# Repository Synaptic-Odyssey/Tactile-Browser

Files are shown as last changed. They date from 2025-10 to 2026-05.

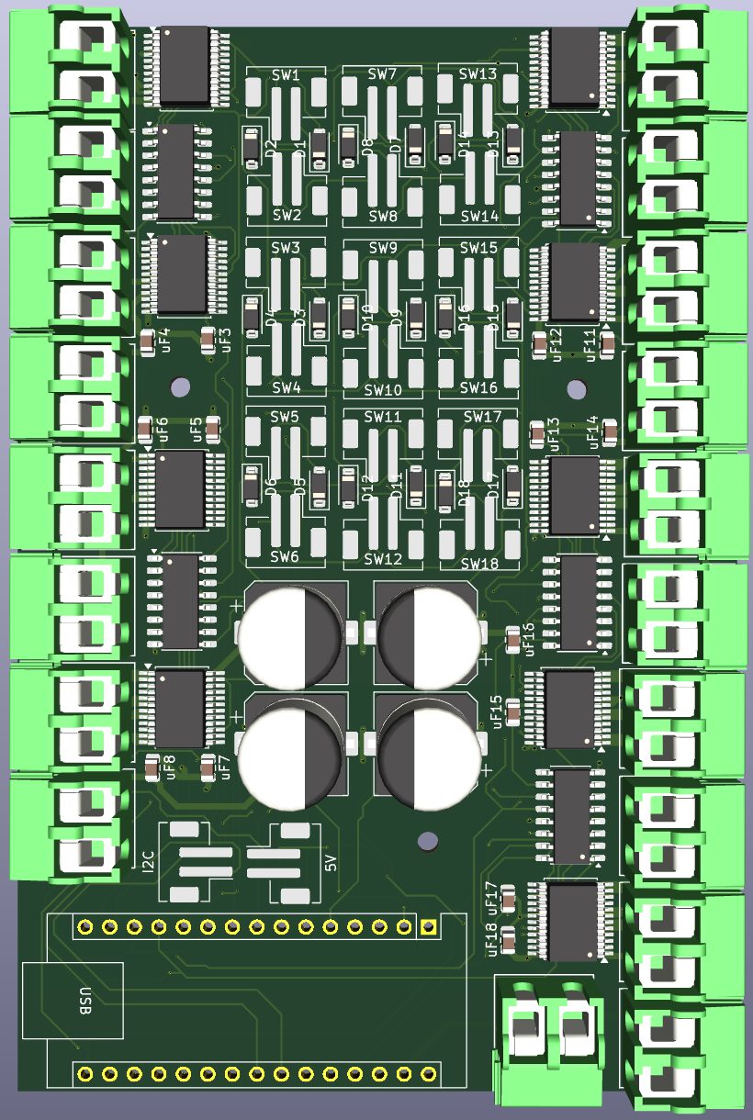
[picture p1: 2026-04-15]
IEEE_MWSCAS/IEEE_MWSCAS_Fig6.png

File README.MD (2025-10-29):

ABSTRACT:

This project aims to develop a tactile web browsing interface for blind and visually impaired users. Current assistive technology, such as screen readers, forces linear navigation through web pages, preventing users from perceiving spatial layout and efficiently locating interactive elements. The proposed system consists of a 17×11 grid of uniform keycaps (with keyswitches that double as input) that move along the Z-axis using bistable solenoids. Each grouping of blocks represents a distinct webpage element (e.g., headers, links, buttons). When a block is pressed down, the system provides audio feedback, reading the element’s content; prolonged touch can select the element and allow the user to interact with it. By mapping webpage structures into a physical tactile representation, users can explore content spatially and intuitively. Estimated cost for the prototype is ~$800. The project timeline spans two quarters, starting implementing webpage-to-grid mapping, then with the creation of a single 2x5 module, before integrating the entire design.

Detailed Presentation: https://docs.google.com/presentation/d/1p2b0jzcivFLc2I2OcCCj18AWDXcFEL55aIJLbLz9RJQ/edit?slide=id.g39ac1d9ecba_0_35#slide=id.g39ac1d9ecba_0_35

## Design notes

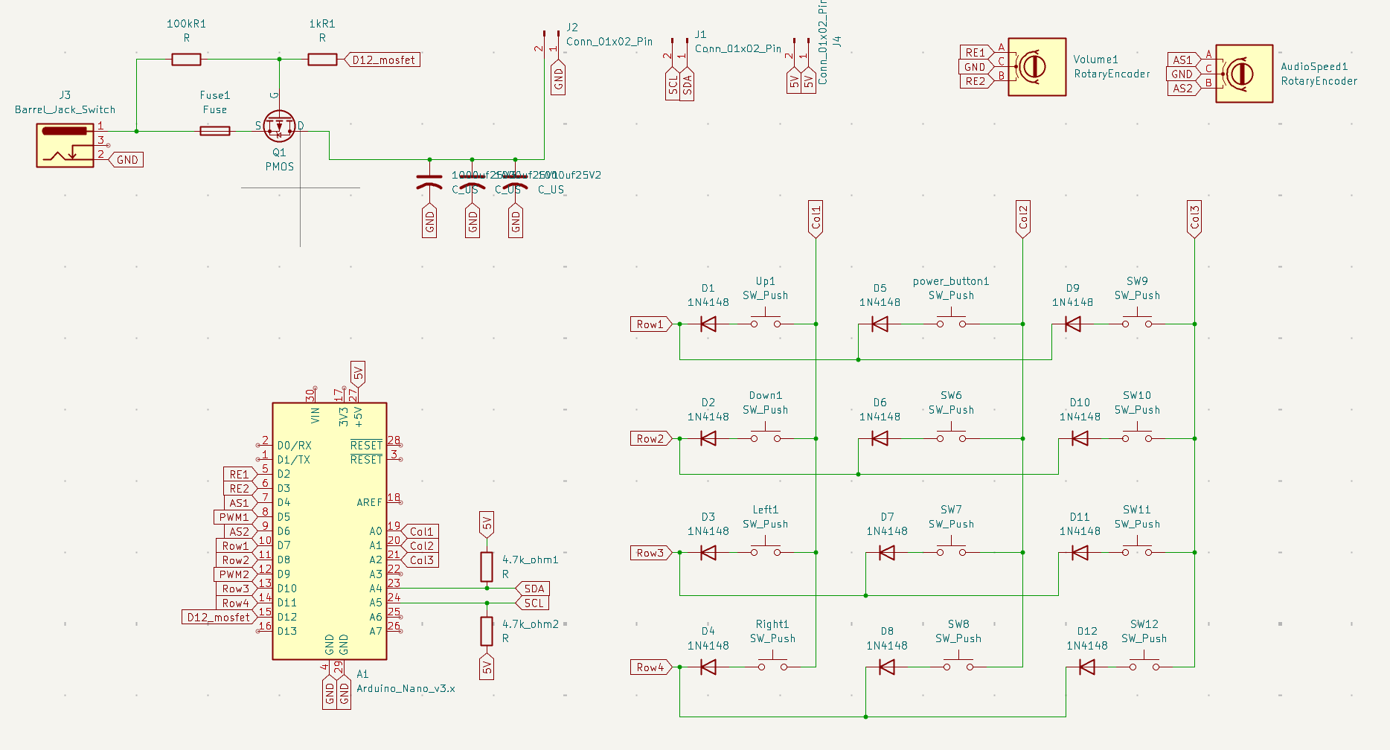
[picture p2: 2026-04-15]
IEEE_MWSCAS/IEEE_MWSCAS_Fig7.png

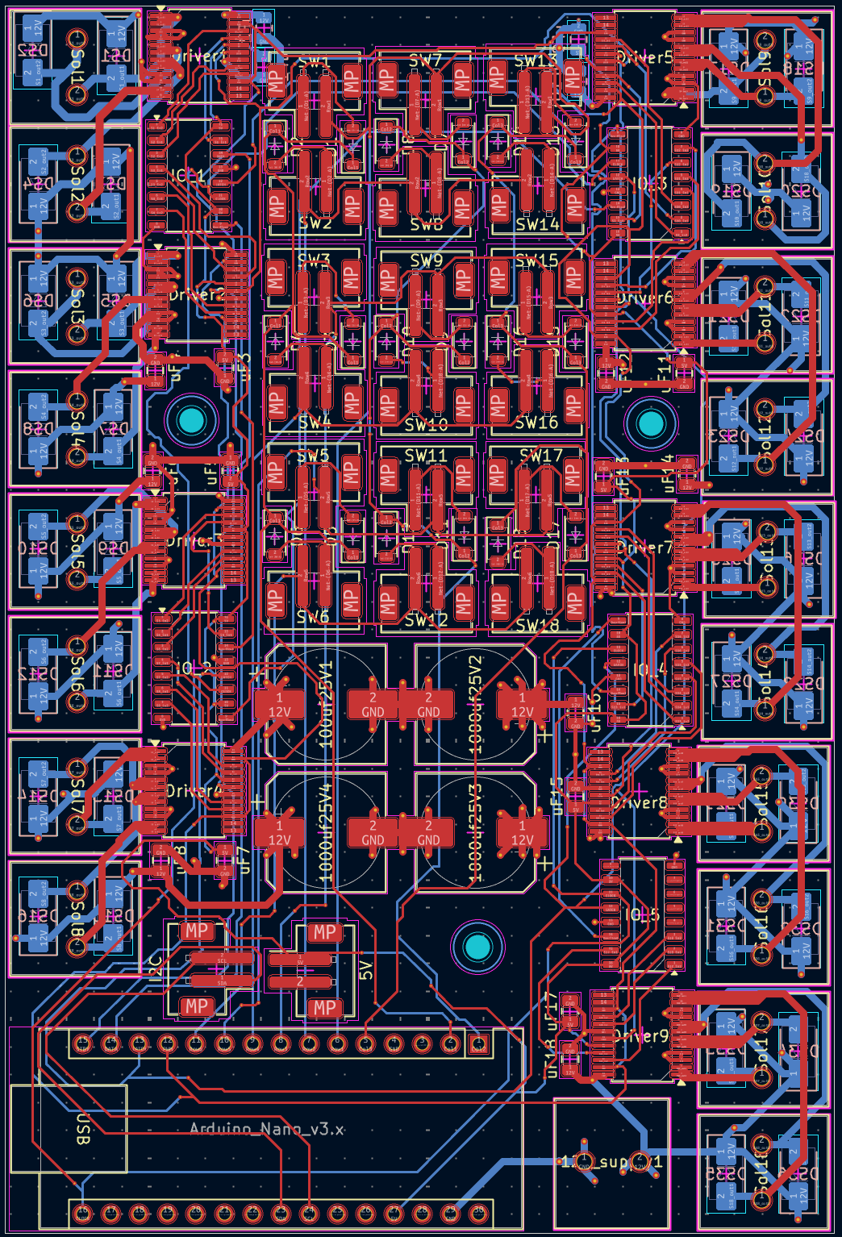
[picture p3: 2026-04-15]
IEEE_MWSCAS/IEEE_MWSCAS_Fig5.png

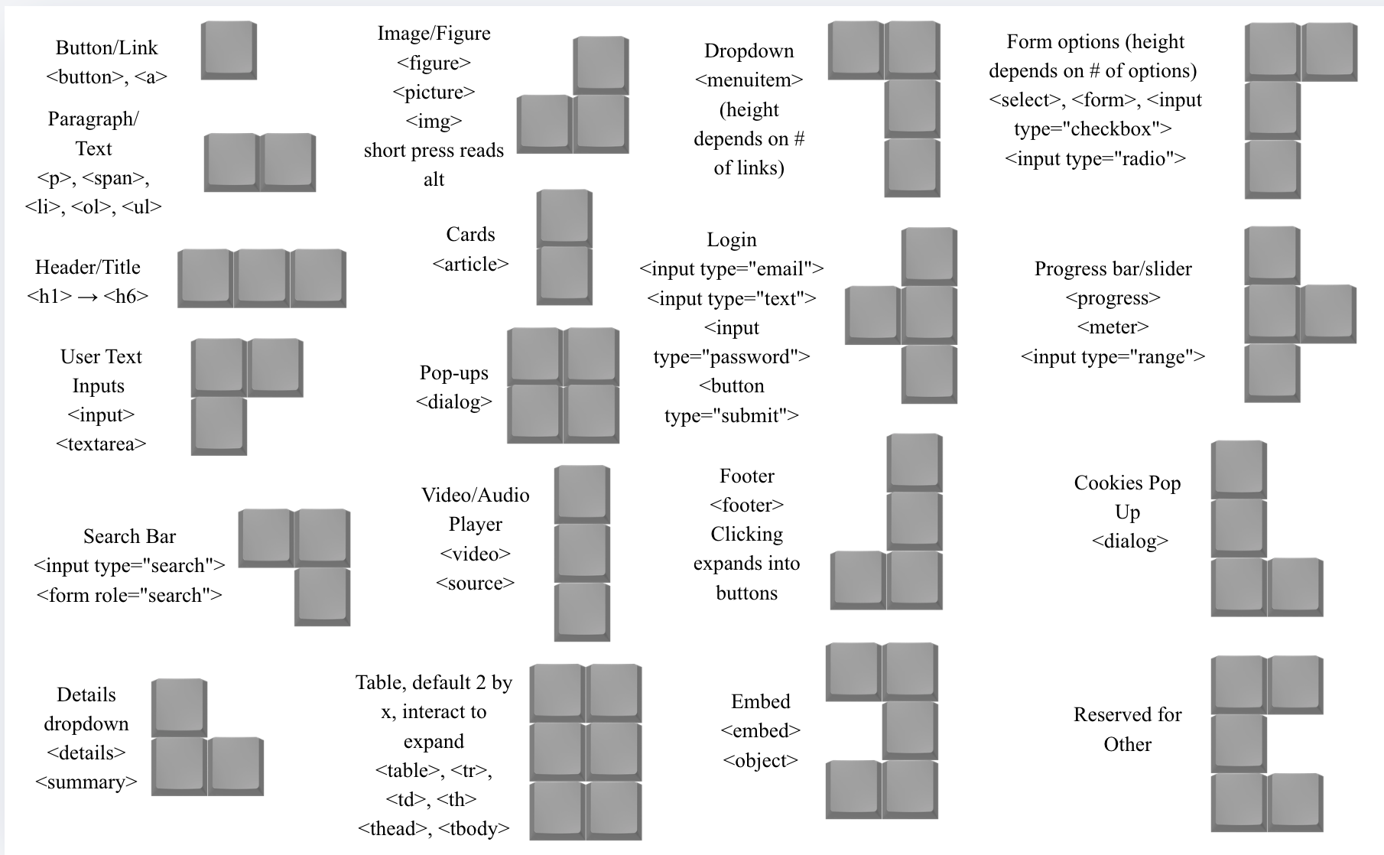
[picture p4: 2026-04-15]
IEEE_MWSCAS/IEEE_MWSCAS_Fig1.png

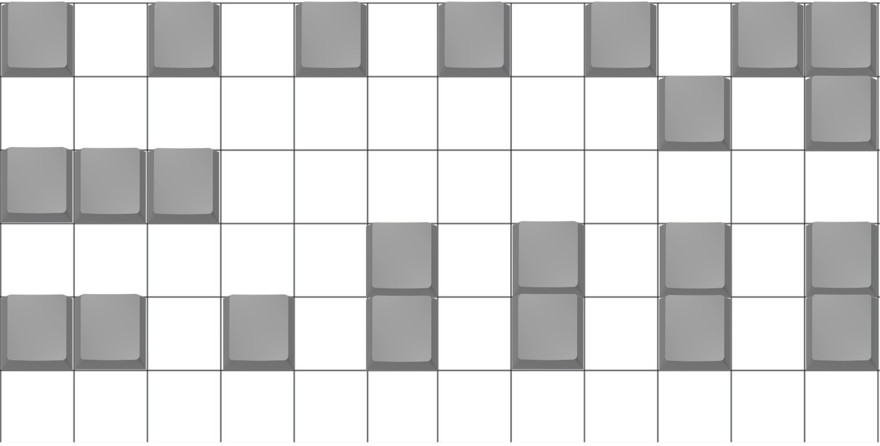
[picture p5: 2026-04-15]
IEEE_MWSCAS/IEEE_MWSCAS_Fig3.png

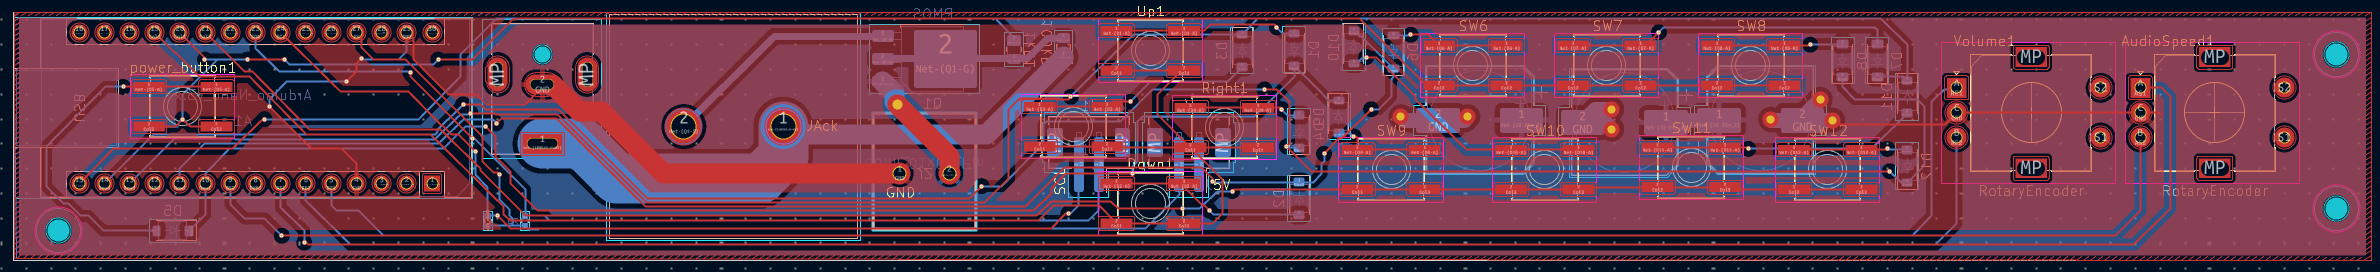
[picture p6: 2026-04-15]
IEEE_MWSCAS/IEEE_MWSCAS_Fig8.png

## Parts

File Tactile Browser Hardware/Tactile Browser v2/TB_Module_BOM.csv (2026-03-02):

Designator | Value | Footprint | Quantity | LCSC Part #
SW3,SW4,SW6,SW17,SW8,SW5,SW9,SW12,SW14,SW10,SW15,SW18,SW16,SW2,SW7,SW1,SW13,SW11 | SW_Push | JST_PH_B2B-PH-SM4-TB_1x02-1MP_P2.00mm_Vertical | 18 | C160352
uF7,uF18,uF8,uF5,uF11,uF16,uF4,uF3,uF12,uF6,uF15,uF14,uF17,uF13,uF2,uF1,uF9,uF10 | C | C_0805_2012Metric | 18 | C141772
Driver8,Driver5,Driver6,Driver7,Driver2,Driver4,Driver1,Driver9,Driver3 | TB6612FNG | SSOP-24_5.3x8.2mm_P0.65mm | 9 | C141517
D1,D14,D13,D3,D7,D18,D9,D10,D17,D2,D16,D8,D15,D5,D11,D6,D12,D4 | 1N4148 | D_SOD-123 | 18 | C917030
1000uf25V2,1000uf25V4,100uf25V1,1000uf25V3 | C_Polarized | CP_Elec_10x12.5 | 4 | C49256851
Sol5,12V_supply1,Sol18,Sol9,Sol17,Sol15,Sol13,Sol14,Sol8,Sol2,Sol7,Sol1,Sol12,Sol3,Sol11,Sol6,Sol16,Sol4,Sol10 | Conn_01x02_Pin | ScrewTerminal_Vertical_1935310 | 19 | C6395113
IO_1,IO_5,IO_4,IO_2,IO_3 | 74HC595 | JEITA_SOIC-16_3.9x9.9mm_P1.27mm | 5 | C5947
5V | Conn_01x01_Pin | JST_PH_B2B-PH-SM4-TB_1x02-1MP_P2.00mm_Vertical | 1 | C160352
I2C | Conn_01x02_Pin | JST_PH_B2B-PH-SM4-TB_1x02-1MP_P2.00mm_Vertical | 1 | C160352
A1 | Arduino_Nano_v3.x | Arduino_Nano | 1 | HAND_SOLDER
DS22,DS10,DS8,DS27,DS9,DS36,DS26,DS12,DS5,DS15,DS19,DS30,DS7,DS1,DS35,DS24,DS3,DS17,DS6,DS34,DS13,DS28,DS25,DS14,DS31,DS2,DS4,DS18,DS16,DS32,DS29,DS21,DS20,DS33,DS23,DS11 | D_Schottky | D_SMA | 36 | C83852

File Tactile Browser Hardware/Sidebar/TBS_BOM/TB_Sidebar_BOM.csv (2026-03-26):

Designator | Comment | Footprint | LCSC Part #
Volume1 | RotaryEncoder | RotaryEncoder_Alps_EC11E-Switch_Vertical_H20mm | HAND_SOLDER
AudioSpeed1 | RotaryEncoder | RotaryEncoder_Alps_EC11E-Switch_Vertical_H20mm | HAND_SOLDER
power_button1 | SW_Push | SW_SPST_EVQQ2 | C2976606
Right1 | SW_Push | SW_SPST_EVQQ2 | C2976606
Down1 | SW_Push | SW_SPST_EVQQ2 | C2976606
SW10 | SW_Push | SW_SPST_EVQQ2 | C2976606
Left1 | SW_Push | SW_SPST_EVQQ2 | C2976606
SW8 | SW_Push | SW_SPST_EVQQ2 | C2976606
SW6 | SW_Push | SW_SPST_EVQQ2 | C2976606
Up1 | SW_Push | SW_SPST_EVQQ2 | C2976606
SW12 | SW_Push | SW_SPST_EVQQ2 | C2976606
SW11 | SW_Push | SW_SPST_EVQQ2 | C2976606
SW7 | SW_Push | SW_SPST_EVQQ2 | C2976606
SW9 | SW_Push | SW_SPST_EVQQ2 | C2976606
1kR1 | R | R_0805_2012Metric | C727989
100kR1 | R | R_0805_2012Metric | C161786
A1 | Arduino_Nano_v3.x | Arduino_Nano | HAND_SOLDER
1000uf25V2 | C_US | CP_Elec_10x12.5 | C49256851
1000uf25V3 | C_US | CP_Elec_10x12.5 | C49256851
1000uf25V1 | C_US | CP_Elec_10x12.5 | C49256851
D8 | 1N4148 | D_SOD-123 | C917030
D9 | 1N4148 | D_SOD-123 | C917030
D10 | 1N4148 | D_SOD-123 | C917030
D5 | 1N4148 | D_SOD-123 | C917030
D6 | 1N4148 | D_SOD-123 | C917030
D12 | 1N4148 | D_SOD-123 | C917030
D11 | 1N4148 | D_SOD-123 | C917030
D3 | 1N4148 | D_SOD-123 | C917030
D2 | 1N4148 | D_SOD-123 | C917030
D1 | 1N4148 | D_SOD-123 | C917030
D4 | 1N4148 | D_SOD-123 | C917030
D7 | 1N4148 | D_SOD-123 | C917030
Q1 | PMOS | TO-252-3_TabPin2 | HAND_SOLDER
Fuse1 | Fuse | FUSE_3560 | HAND_SOLDER
J2 | Conn_01x02_Pin | ScrewTerminal_Vertical_1935310 | HAND_SOLDER
J4 | Conn_01x02_Pin | JST_PH_B2B-PH-SM4-TB_1x02-1MP_P2.00mm_Vertical | C160352
J1 | Conn_01x02_Pin | JST_PH_B2B-PH-SM4-TB_1x02-1MP_P2.00mm_Vertical | C160352
4.7k_ohm2 | R | R_0402_1005Metric | C105871
4.7k_ohm1 | R | R_0402_1005Metric | C105871
J3 | Barrel_Jack_Switch | BarrelJack_CUI_PJ-063AH_Horizontal | HAND_SOLDER

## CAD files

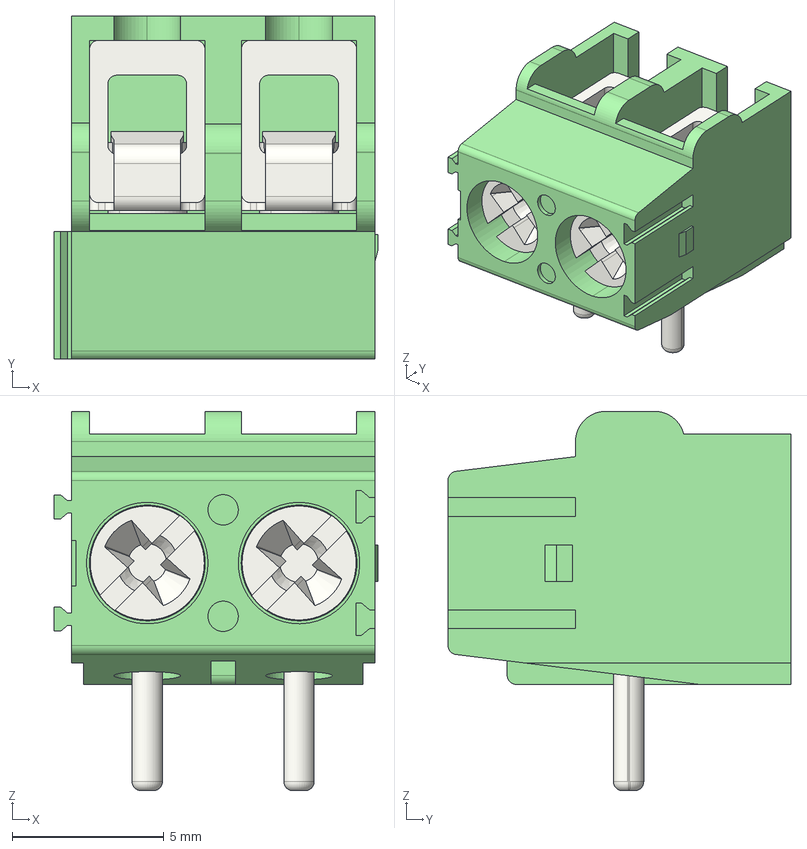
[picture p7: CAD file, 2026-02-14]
Tactile Browser Hardware/Tactile Browser v2/pxc_1935310_07_02_PT-1-5-2-5-0-V_3D.stp
10.7 x 11.3 x 12.5 mm

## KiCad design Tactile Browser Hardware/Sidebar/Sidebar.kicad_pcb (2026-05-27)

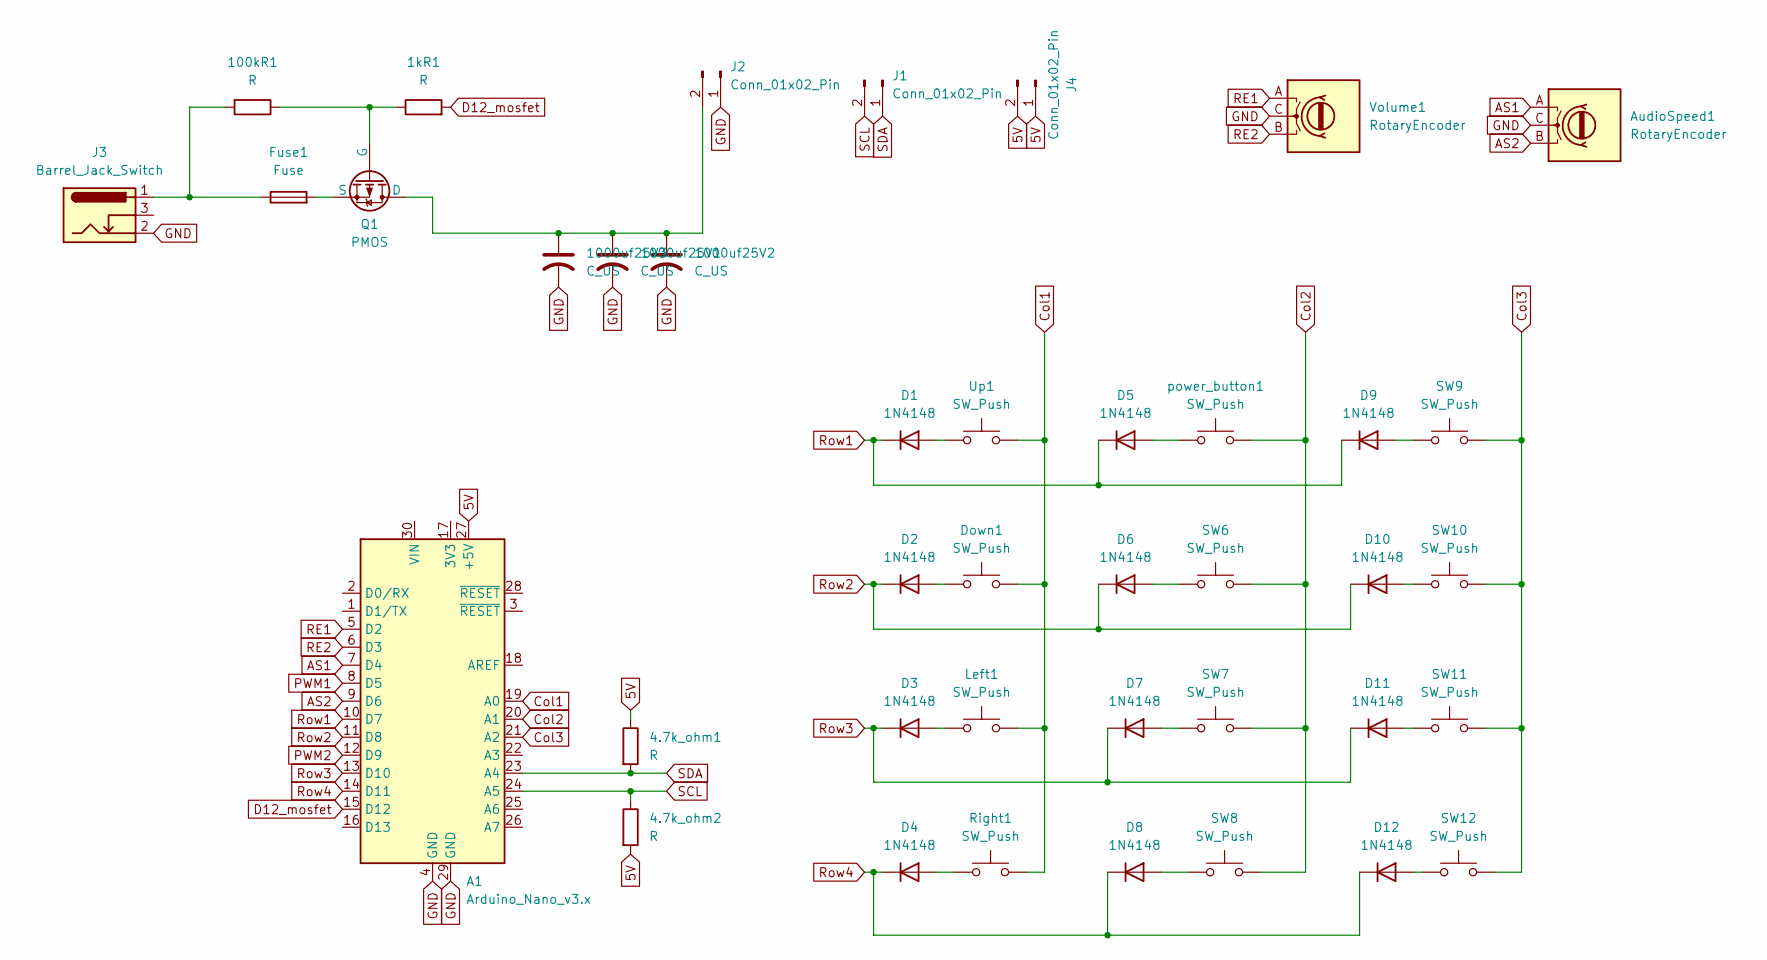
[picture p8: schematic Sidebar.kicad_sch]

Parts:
1kR1, 100kR1: R; R_0805_2012Metric
4.7k_ohm1, 4.7k_ohm2: R; R_0402_1005Metric
1000uf25V1, 1000uf25V2, 1000uf25V3: C_US; CP_Elec_10x12.5
A1: Arduino_Nano_v3.x; Arduino_Nano
AudioSpeed1: RotaryEncoder; RotaryEncoder_Alps_EC11E-Switch_Vertical_H20mm
D1, D2, D3, D4, D5, D6, D7, D8, D9, D10, D11, D12: 1N4148; D_SOD-123
Down1: SW_Push; SW_SPST_EVQQ2
Fuse1: Fuse; FUSE_3560
J1, J4: Conn_01x02_Pin; JST_PH_B2B-PH-SM4-TB_1x02-1MP_P2.00mm_Vertical
J2: Conn_01x02_Pin; ScrewTerminal_Vertical_1935310
J3: Barrel_Jack_Switch; BarrelJack_CUI_PJ-063AH_Horizontal
Left1: SW_Push; SW_SPST_EVQQ2
Q1: PMOS; TO-252-3_TabPin2
Right1: SW_Push; SW_SPST_EVQQ2
SW6, SW7, SW8, SW9, SW10, SW11, SW12: SW_Push; SW_SPST_EVQQ2
Up1: SW_Push; SW_SPST_EVQQ2
Volume1: RotaryEncoder; RotaryEncoder_Alps_EC11E-Switch_Vertical_H20mm
power_button1: SW_Push; SW_SPST_EVQQ2

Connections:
5V: 4.7k_ohm1.1, 4.7k_ohm2.2, A1.27 (+5V), J4.1, J4.2
AS1: A1.7 (D4), AudioSpeed1.A
AS2: A1.9 (D6), AudioSpeed1.B
Col1: A1.19 (A0), Down1.2, Left1.2, Right1.2, Up1.2
Col2: A1.20 (A1), SW6.2, SW7.2, SW8.2, power_button1.2
Col3: A1.21 (A2), SW9.2, SW10.2, SW11.2, SW12.2
D12_mosfet: 1kR1.2, A1.15 (D12); also elsewhere on the board
GND: 1000uf25V1.2, 1000uf25V2.2, 1000uf25V3.2, A1.4 (GND), A1.29 (GND), AudioSpeed1.C, J2.1, J3.2, Volume1.C
unnamed 8: 100kR1.2, Fuse1.1, J3.1; also elsewhere on the board
unnamed: D1.2 (A), Up1.1
unnamed: D2.2 (A), Down1.1
unnamed: D3.2 (A), Left1.1
unnamed: D4.2 (A), Right1.1
unnamed: D5.2 (A), power_button1.1
unnamed: D6.2 (A), SW6.1
unnamed: D7.2 (A), SW7.1
unnamed: D8.2 (A), SW8.1
unnamed: D9.2 (A), SW9.1
unnamed: D10.2 (A), SW10.1
unnamed: D11.2 (A), SW11.1
unnamed: D12.2 (A), SW12.1
unnamed: 1000uf25V1.1, 1000uf25V2.1, 1000uf25V3.1, J2.2, Q1.1 (D)
unnamed 22: 1kR1.1, 100kR1.1, Q1.2 (G); also elsewhere on the board
unnamed: Fuse1.2, Q1.3 (S)
PWM1: A1.8 (D5)
PWM2: A1.12 (D9)
RE1: A1.5 (D2), Volume1.A
RE2: A1.6 (D3), Volume1.B
Row1: A1.10 (D7), D1.1 (K), D5.1 (K), D9.1 (K)
Row2: A1.11 (D8), D2.1 (K), D6.1 (K), D10.1 (K)
Row3: A1.13 (D10), D3.1 (K), D7.1 (K), D11.1 (K)
Row4: A1.14 (D11), D4.1 (K), D8.1 (K), D12.1 (K)
SCL: 4.7k_ohm2.1, A1.24 (A5), J1.2
SDA: 4.7k_ohm1.2, A1.23 (A4), J1.1

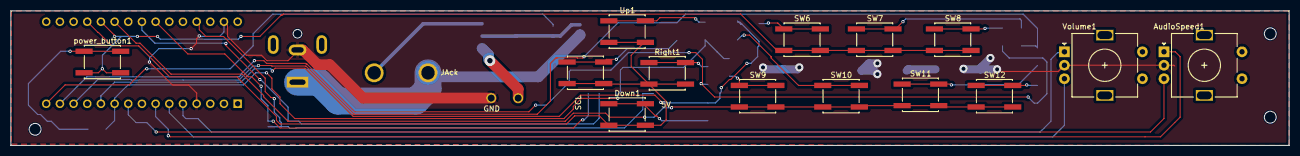
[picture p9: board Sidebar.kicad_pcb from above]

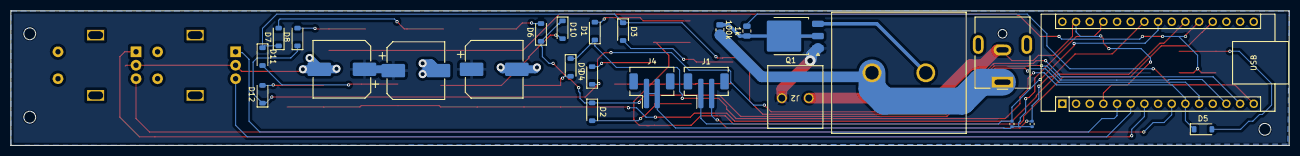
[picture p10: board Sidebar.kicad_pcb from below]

Board: 2 copper layers, 237.5 x 25.0 mm, 40 parts (26 on the bottom side), 32 nets.

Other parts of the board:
1k, 100k: R; R_0805_2012Metric

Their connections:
D12_mosfet: 1k.2; also elsewhere on the board
unnamed 8: 100k.2; also elsewhere on the board
unnamed 22: 1k.1, 100k.1; also elsewhere on the board

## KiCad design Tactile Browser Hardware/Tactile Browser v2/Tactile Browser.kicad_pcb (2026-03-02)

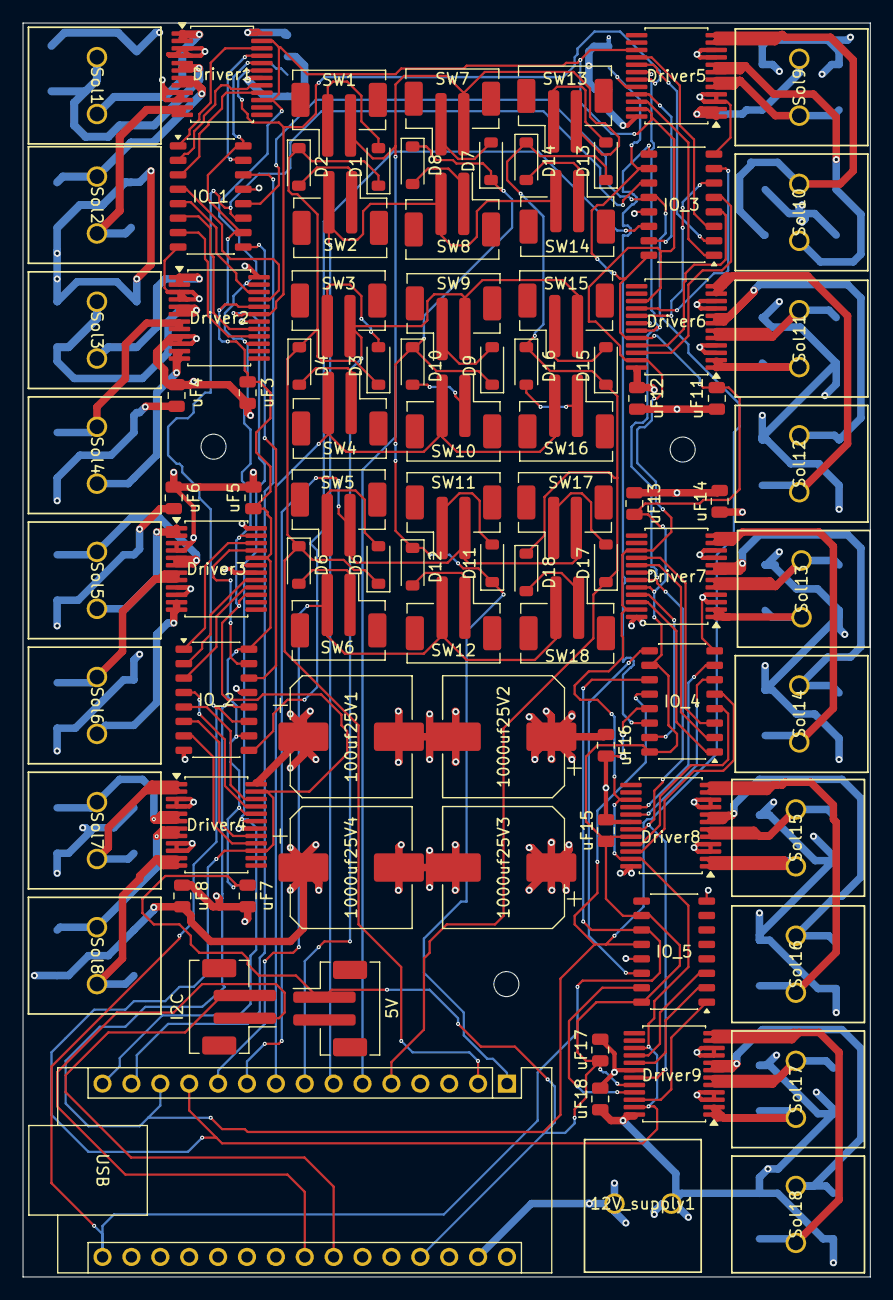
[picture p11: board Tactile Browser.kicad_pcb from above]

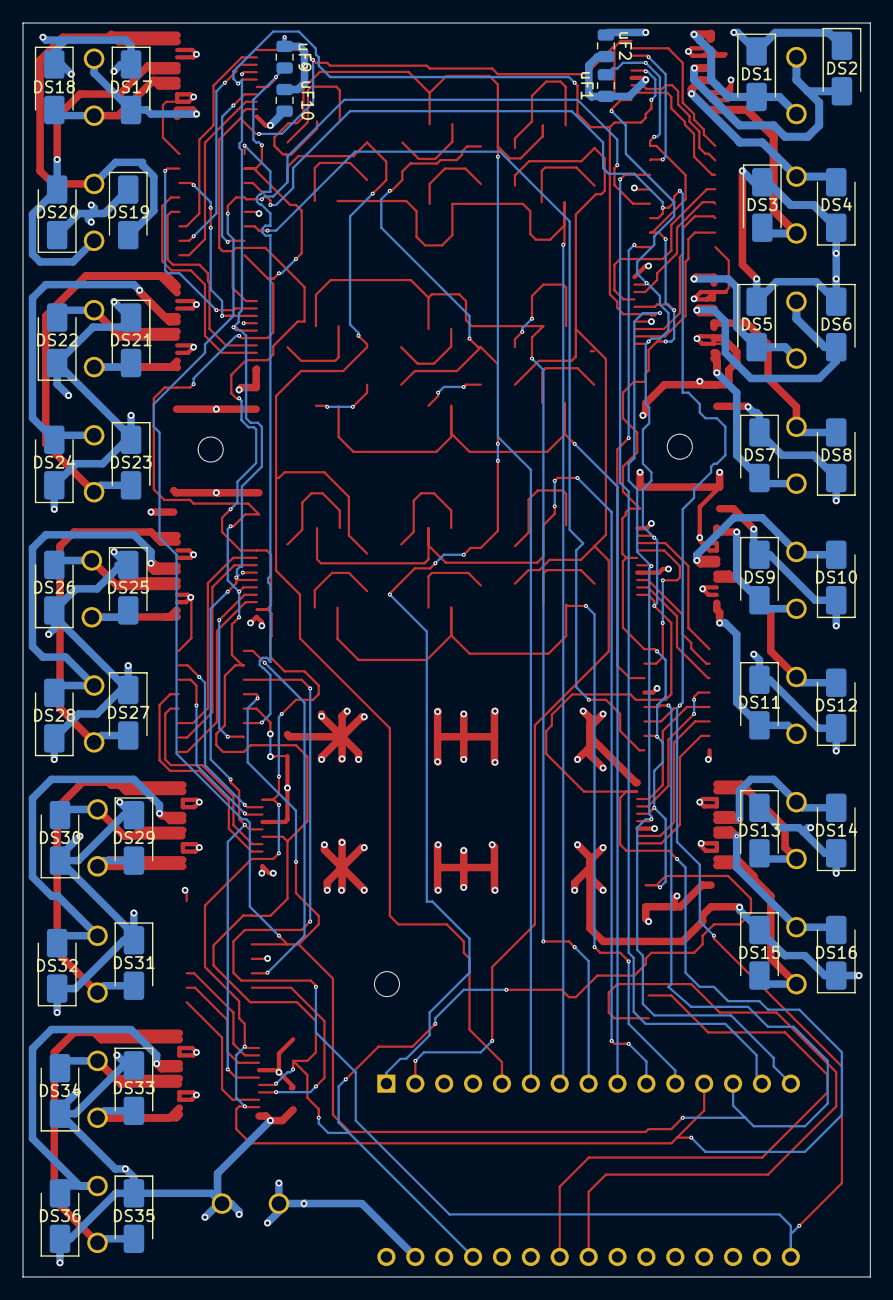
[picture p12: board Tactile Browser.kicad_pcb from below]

Board: 4 copper layers, 74.5 x 110.2 mm, 130 parts (40 on the bottom side), 113 nets.

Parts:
5V: Conn_01x01_Pin; JST_PH_B2B-PH-SM4-TB_1x02-1MP_P2.00mm_Vertical
12V_supply1: Conn_01x02_Pin; ScrewTerminal_Vertical_1935310
100uf25V1, 1000uf25V2, 1000uf25V3, 1000uf25V4: C_Polarized; CP_Elec_10x12.5
A1: Arduino_Nano_v3.x; Arduino_Nano
D1, D2, D3, D4, D5, D6, D7, D8, D9, D10, D11, D12, D13, D14, D15, D16, D17, D18: 1N4148; D_SOD-123
DS1, DS2, DS3, DS4, DS5, DS6, DS7, DS8, DS9, DS10, DS11, DS12, DS13, DS14, DS15, DS16, DS17, DS18, DS19, DS20, DS21, DS22, DS23, DS24, DS25, DS26, DS27, DS28, DS29, DS30, DS31, DS32, DS33, DS34, DS35, DS36: D_Schottky; D_SMA
Driver1, Driver2, Driver3, Driver4, Driver5, Driver6, Driver7, Driver8, Driver9: TB6612FNG; SSOP-24_5.3x8.2mm_P0.65mm
I2C: Conn_01x02_Pin; JST_PH_B2B-PH-SM4-TB_1x02-1MP_P2.00mm_Vertical
IO_1, IO_2, IO_3, IO_4, IO_5: 74HC595; JEITA_SOIC-16_3.9x9.9mm_P1.27mm
SW1, SW2, SW3, SW4, SW5, SW6, SW7, SW8, SW9, SW10, SW11, SW12, SW13, SW14, SW15, SW16, SW17, SW18: SW_Push; JST_PH_B2B-PH-SM4-TB_1x02-1MP_P2.00mm_Vertical
Sol1, Sol2, Sol3, Sol4, Sol5, Sol6, Sol7, Sol8, Sol9, Sol10, Sol11, Sol12, Sol13, Sol14, Sol15, Sol16, Sol17, Sol18: Conn_01x02_Pin; ScrewTerminal_Vertical_1935310
uF1, uF2, uF3, uF4, uF5, uF6, uF7, uF8, uF9, uF10, uF11, uF12, uF13, uF14, uF15, uF16, uF17, uF18: C; C_0805_2012Metric

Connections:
5V: 5V.1, A1.27 (+5V), Driver1.20 (VCC), Driver2.20 (VCC), Driver3.20 (VCC), Driver4.20 (VCC), Driver5.20 (VCC), Driver6.20 (VCC), Driver7.20 (VCC), Driver8.20 (VCC), Driver9.20 (VCC), IO_1.10 (~SRCLR), IO_1.16 (VCC), IO_2.10 (~SRCLR), IO_2.16 (VCC), IO_3.10 (~SRCLR), IO_3.16 (VCC), IO_4.10 (~SRCLR), IO_4.16 (VCC), IO_5.10 (~SRCLR), IO_5.16 (VCC), uF1.2, uF3.2, uF5.2, uF7.1, uF9.1, uF11.1, uF13.1, uF15.1, uF17.1
12V: 12V_supply1.2, 100uf25V1.1, 1000uf25V2.1, 1000uf25V3.1, 1000uf25V4.1, DS1.1 (K), DS2.1 (K), DS3.1 (K), DS4.1 (K), DS5.1 (K), DS6.1 (K), DS7.1 (K), DS8.1 (K), DS9.1 (K), DS10.1 (K), DS11.1 (K), DS12.1 (K), DS13.1 (K), DS14.1 (K), DS15.1 (K), DS16.1 (K), DS17.1 (K), DS18.1 (K), DS19.1 (K), DS20.1 (K), DS21.1 (K), DS22.1 (K), DS23.1 (K), DS24.1 (K), DS25.1 (K), DS26.1 (K), DS27.1 (K), DS28.1 (K), DS29.1 (K), DS30.1 (K), DS31.1 (K), DS32.1 (K), DS33.1 (K), DS34.1 (K), DS35.1 (K), DS36.1 (K), Driver1.24 (VM1), Driver2.24 (VM3), Driver3.24 (VM1), Driver4.24 (VM1), Driver5.24 (VM3), Driver6.24 (VM1), Driver7.24 (VM3), Driver8.24 (VM3), Driver9.24 (VM3), uF2.1, uF4.1, uF6.1, uF8.1, uF10.1, uF12.1, uF14.1, uF16.1, uF18.1
CLOCK: A1.16 (D13), IO_1.11 (SRCLK), IO_2.11 (SRCLK), IO_3.11 (SRCLK), IO_4.11 (SRCLK), IO_5.11 (SRCLK)
Col1: A1.2 (D0/RX), D1.1 (K), D2.1 (K), D3.1 (K), D4.1 (K), D5.1 (K), D6.1 (K)
Col2: A1.1 (D1/TX), D7.1 (K), D8.1 (K), D9.1 (K), D10.1 (K), D11.1 (K), D12.1 (K)
Col3: A1.5 (D2), D13.1 (K), D14.1 (K), D15.1 (K), D16.1 (K), D17.1 (K), D18.1 (K)
DATA: A1.14 (D11), IO_1.14 (SER)
GND: 12V_supply1.1, 100uf25V1.2, 1000uf25V2.2, 1000uf25V3.2, 1000uf25V4.2, A1.4 (GND), A1.29 (GND), Driver1.3 (PGND1), Driver1.4 (PGND1), Driver1.9 (PGND2), Driver1.10 (PGND2), Driver1.18 (GND), Driver2.3 (PGND1), Driver2.4 (PGND1), Driver2.9 (PGND2), Driver2.10 (PGND2), Driver2.18 (GND), Driver3.3 (PGND1), Driver3.4 (PGND1), Driver3.9 (PGND2), Driver3.10 (PGND2), Driver3.18 (GND), Driver4.3 (PGND1), Driver4.4 (PGND1), Driver4.9 (PGND2), Driver4.10 (PGND2), Driver4.18 (GND), Driver5.3 (PGND1), Driver5.4 (PGND1), Driver5.9 (PGND2), Driver5.10 (PGND2), Driver5.18 (GND), Driver6.3 (PGND1), Driver6.4 (PGND1), Driver6.9 (PGND2), Driver6.10 (PGND2), Driver6.18 (GND), Driver7.3 (PGND1), Driver7.4 (PGND1), Driver7.9 (PGND2), Driver7.10 (PGND2), Driver7.18 (GND), Driver8.3 (PGND1), Driver8.4 (PGND1), Driver8.9 (PGND2), Driver8.10 (PGND2), Driver8.18 (GND), Driver9.3 (PGND1), Driver9.4 (PGND1), Driver9.9 (PGND2), Driver9.10 (PGND2), Driver9.18 (GND), IO_1.8 (GND), IO_1.13 (~OE), IO_2.8 (GND), IO_2.13 (~OE), IO_3.8 (GND), IO_3.13 (~OE), IO_4.8 (GND), IO_4.13 (~OE), IO_5.8 (GND), IO_5.13 (~OE), uF1.1, uF2.2, uF3.1, uF4.2, uF5.1, uF6.2, uF7.2, uF8.2, uF9.2, uF10.2, uF11.2, uF12.2, uF13.2, uF14.2, uF15.2, uF16.2, uF17.2, uF18.2
LATCH: A1.13 (D10), IO_1.12 (RCLK), IO_2.12 (RCLK), IO_3.12 (RCLK), IO_4.12 (RCLK), IO_5.12 (RCLK)
unnamed: D1.2 (A), SW1.1
unnamed: D2.2 (A), SW2.1
unnamed: D3.2 (A), SW3.1
unnamed: D4.2 (A), SW4.1
unnamed: D5.2 (A), SW5.1
unnamed: D6.2 (A), SW6.1
unnamed: D7.2 (A), SW7.1
unnamed: D8.2 (A), SW8.1
unnamed: D9.2 (A), SW9.1
unnamed: D10.2 (A), SW10.1
unnamed: D11.2 (A), SW11.1
unnamed: D12.2 (A), SW12.1
unnamed: D13.2 (A), SW13.1
unnamed: D14.2 (A), SW14.1
unnamed: D15.2 (A), SW15.1
unnamed: D16.2 (A), SW16.1
unnamed: D17.2 (A), SW17.1
unnamed: D18.2 (A), SW18.1
Overflow1: IO_1.9 (QH'), IO_2.14 (SER)
Overflow2: IO_2.9 (QH'), IO_3.14 (SER)
Overflow3: IO_3.9 (QH'), IO_4.14 (SER)
Overflow4: IO_4.9 (QH'), IO_5.14 (SER)
PWM: A1.12 (D9), Driver1.15 (PWMB), Driver1.23 (PWMA), Driver2.15 (PWMB), Driver2.23 (PWMA), Driver3.15 (PWMB), Driver3.23 (PWMA), Driver4.15 (PWMB), Driver4.23 (PWMA), Driver5.15 (PWMB), Driver5.23 (PWMA), Driver6.15 (PWMB), Driver6.23 (PWMA), Driver7.15 (PWMB), Driver7.23 (PWMA), Driver8.15 (PWMB), Driver8.23 (PWMA), Driver9.15 (PWMB), Driver9.23 (PWMA)
Row1: A1.6 (D3), SW1.2, SW7.2, SW13.2
Row2: A1.7 (D4), SW2.2, SW8.2, SW14.2
Row3: A1.8 (D5), SW3.2, SW9.2, SW15.2
Row4: A1.9 (D6), SW4.2, SW10.2, SW16.2
Row5: A1.10 (D7), SW5.2, SW11.2, SW17.2
Row6: A1.11 (D8), SW6.2, SW12.2, SW18.2
S1_in1: Driver1.21 (AIN1), IO_1.15 (QA)
S1_in2: Driver1.22 (AIN2), IO_1.1 (QB)
S1_out1: DS1.2 (A), Driver1.1 (AO1), Driver1.2 (AO1), Sol1.2
S1_out2: DS2.2 (A), Driver1.5 (AO2), Driver1.6 (AO2), Sol1.1
S2_in1: Driver1.17 (BIN1), IO_1.2 (QC)
S2_in2: Driver1.16 (BIN2), IO_1.3 (QD)
S2_out1: DS3.2 (A), Driver1.11 (BO1), Driver1.12 (BO1), Sol2.2
S2_out2: DS4.2 (A), Driver1.7 (BO2), Driver1.8 (BO2), Sol2.1
S3_in1: Driver2.21 (AIN1), IO_1.4 (QE)
S3_in2: Driver2.22 (AIN2), IO_1.5 (QF)
S3_out1: DS5.2 (A), Driver2.1 (AO1), Driver2.2 (AO1), Sol3.2
S3_out2: DS6.2 (A), Driver2.5 (AO2), Driver2.6 (AO2), Sol3.1
S4_in1: Driver2.17 (BIN1), IO_1.6 (QG)
S4_in2: Driver2.16 (BIN2), IO_1.7 (QH)
S4_out1: DS7.2 (A), Driver2.11 (BO1), Driver2.12 (BO1), Sol4.2
S4_out2: DS8.2 (A), Driver2.7 (BO2), Driver2.8 (BO2), Sol4.1
S5_in1: Driver3.21 (AIN1), IO_2.15 (QA)
S5_in2: Driver3.22 (AIN2), IO_2.1 (QB)
S5_out1: DS9.2 (A), Driver3.1 (AO1), Driver3.2 (AO1), Sol5.2
S5_out2: DS10.2 (A), Driver3.5 (AO2), Driver3.6 (AO2), Sol5.1
S6_in1: Driver3.17 (BIN1), IO_2.2 (QC)
S6_in2: Driver3.16 (BIN2), IO_2.3 (QD)
S6_out1: DS11.2 (A), Driver3.11 (BO1), Driver3.12 (BO1), Sol6.2
S6_out2: DS12.2 (A), Driver3.7 (BO2), Driver3.8 (BO2), Sol6.1
S7_in1: Driver4.21 (AIN1), IO_2.4 (QE)
S7_in2: Driver4.22 (AIN2), IO_2.5 (QF)
S7_out1: DS13.2 (A), Driver4.1 (AO1), Driver4.2 (AO1), Sol7.2
S7_out2: DS14.2 (A), Driver4.5 (AO2), Driver4.6 (AO2), Sol7.1
S8_in1: Driver4.17 (BIN1), IO_2.6 (QG)
S8_in2: Driver4.16 (BIN2), IO_2.7 (QH)
S8_out1: DS15.2 (A), Driver4.11 (BO1), Driver4.12 (BO1), Sol8.2
S8_out2: DS16.2 (A), Driver4.7 (BO2), Driver4.8 (BO2), Sol8.1
S9_in1: Driver5.21 (AIN1), IO_3.15 (QA)
S9_in2: Driver5.22 (AIN2), IO_3.1 (QB)
S9_out1: DS17.2 (A), Driver5.1 (AO1), Driver5.2 (AO1), Sol9.2
S9_out2: DS18.2 (A), Driver5.5 (AO2), Driver5.6 (AO2), Sol9.1
S10_in1: Driver5.17 (BIN1), IO_3.2 (QC)
S10_in2: Driver5.16 (BIN2), IO_3.3 (QD)
S10_out1: DS19.2 (A), Driver5.11 (BO1), Driver5.12 (BO1), Sol10.2
S10_out2: DS20.2 (A), Driver5.7 (BO2), Driver5.8 (BO2), Sol10.1
S11_in1: Driver6.21 (AIN1), IO_3.4 (QE)
S11_in2: Driver6.22 (AIN2), IO_3.5 (QF)
S11_out1: DS21.2 (A), Driver6.1 (AO1), Driver6.2 (AO1), Sol11.1
S11_out2: DS22.2 (A), Driver6.5 (AO2), Driver6.6 (AO2), Sol11.2
S12_in1: Driver6.17 (BIN1), IO_3.6 (QG)
S12_in2: Driver6.16 (BIN2), IO_3.7 (QH)
S12_out1: DS23.2 (A), Driver6.11 (BO1), Driver6.12 (BO1), Sol12.1
S12_out2: DS24.2 (A), Driver6.7 (BO2), Driver6.8 (BO2), Sol12.2
S13_in1: Driver7.21 (AIN1), IO_4.15 (QA)
S13_in2: Driver7.22 (AIN2), IO_4.1 (QB)
S13_out1: DS25.2 (A), Driver7.1 (AO1), Driver7.2 (AO1), Sol13.1
S13_out2: DS26.2 (A), Driver7.5 (AO2), Driver7.6 (AO2), Sol13.2
S14_in1: Driver7.17 (BIN1), IO_4.2 (QC)
S14_in2: Driver7.16 (BIN2), IO_4.3 (QD)
S14_out1: DS27.2 (A), Driver7.11 (BO1), Driver7.12 (BO1), Sol14.1
S14_out2: DS28.2 (A), Driver7.7 (BO2), Driver7.8 (BO2), Sol14.2
S15_in1: Driver8.21 (AIN1), IO_4.4 (QE)
S15_in2: Driver8.22 (AIN2), IO_4.5 (QF)
S15_out1: DS29.2 (A), Driver8.1 (AO1), Driver8.2 (AO1), Sol15.1
S15_out2: DS30.2 (A), Driver8.5 (AO2), Driver8.6 (AO2), Sol15.2
S16_in1: Driver8.17 (BIN1), IO_4.6 (QG)
S16_in2: Driver8.16 (BIN2), IO_4.7 (QH)
S16_out1: DS31.2 (A), Driver8.11 (BO1), Driver8.12 (BO1), Sol16.1
S16_out2: DS32.2 (A), Driver8.7 (BO2), Driver8.8 (BO2), Sol16.2
S17_in1: Driver9.21 (AIN1), IO_5.15 (QA)
S17_in2: Driver9.22 (AIN2), IO_5.1 (QB)
S17_out1: DS33.2 (A), Driver9.1 (AO1), Driver9.2 (AO1), Sol17.1
S17_out2: DS34.2 (A), Driver9.5 (AO2), Driver9.6 (AO2), Sol17.2
S18_in1: Driver9.17 (BIN1), IO_5.2 (QC)
S18_in2: Driver9.16 (BIN2), IO_5.3 (QD)
S18_out1: DS35.2 (A), Driver9.11 (BO1), Driver9.12 (BO1), Sol18.1
S18_out2: DS36.2 (A), Driver9.7 (BO2), Driver9.8 (BO2), Sol18.2
SCL: A1.24 (A5), I2C.2
SDA: A1.23 (A4), I2C.1
STBY: A1.15 (D12), Driver1.19 (STBY), Driver2.19 (STBY), Driver3.19 (STBY), Driver4.19 (STBY), Driver5.19 (STBY), Driver6.19 (STBY), Driver7.19 (STBY), Driver8.19 (STBY), Driver9.19 (STBY)

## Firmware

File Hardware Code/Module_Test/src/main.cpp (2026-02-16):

#include <Arduino.h>
#include <SPI.h>


const uint8_t CLOCK_PIN = 13;
const uint8_t DATA_PIN = 11;
const uint8_t LATCH_PIN = 10;

uint8_t sr[5];

//TB6612
const uint8_t STBY_PIN = 12;

constexpr uint8_t bitByte(uint8_t bit) {
  return bit / 8;
}

constexpr uint8_t bitMask(uint8_t bit) {
  return 1 << (bit % 8);
}

void setSolenoid(uint8_t solenoid, bool up);
void updateShiftRegisters();


void setup() {

  pinMode(LATCH_PIN, OUTPUT);
  digitalWrite(LATCH_PIN, LOW);

  pinMode(STBY_PIN, OUTPUT);
  digitalWrite(STBY_PIN, HIGH);



  SPI.begin();

}


void loop() {

  setSolenoid(0, false);
  setSolenoid(1, false);
  updateShiftRegisters();
  delay(3000);

  setSolenoid(0, true);
  setSolenoid(1, true);
  updateShiftRegisters();
  delay(3000);
}

//the 74hc595s control solenoids 4-20 but will be numbered 0-16 in code
//returns the bitmask for the given solenoid number
//solenoids are numbered from 0 
//TODO: get rid of bool up, instead just check the sr[] for which solenoids are up or down, then invert the pulse to the tb6612
//TODO: move the remaining 3 solenoids to the 5th 74hc595, so all solenoids can be numbered uniformly
void setSolenoid(uint8_t solenoid, bool up) {

  uint8_t in1_bit = solenoid * 2;
  uint8_t in2_bit = solenoid * 2 + 1;

  //test which is the right direction
  if (up) {
    //this is putting down the solenoid
    sr[bitByte(in1_bit)] |= bitMask(in1_bit);
    sr[bitByte(in2_bit)] &= ~bitMask(in2_bit);
  } else {
    sr[bitByte(in1_bit)] &= ~bitMask(in1_bit);
    sr[bitByte(in2_bit)] |= bitMask(in2_bit);
  }
}


void updateShiftRegisters() {

  digitalWrite(LATCH_PIN, LOW);

  for (int i = 4; i >= 0; i--) {
    SPI.transfer(sr[i]);
  }

  digitalWrite(LATCH_PIN, HIGH);
}

/*
Issue with the code above, doesn't set pulses (20ms max [try lowering it], 20% duty cycle)
Code below for the single solenoid (the reason it was so loud is because 
it was drawing as much amps as it could since I connected the power source to just
one solnoid)
*/

/*

// ----------------------
// Arduino Nano → 74HC595 → TB6612FNG → Bistable Solenoid
// ----------------------

// 74HC595 pins
const int LATCH_PIN = 10;  // RCLK
const int DATA_PIN  = 11;  // SER
const int CLOCK_PIN = 13;  // SRCLK

// TB6612FNG pins
const int PWM_PIN   = 9;   // PWMA
const int STBY_PIN  = 12;  // STBY

// Bit positions in the 74HC595
// QA = bit 0
// QB = bit 1
const int AIN1_BIT = 0;
const int AIN2_BIT = 1;

// Solenoid pulse parameters
const int PULSE_MS = 20;        // pulse duration in ms
const int WAIT_MS  = 2000;      // wait between pulses
const int CYCLES   = 10;        // number of forward/backward cycles

void setup() {
  // 74HC595 pins
  pinMode(LATCH_PIN, OUTPUT);
  pinMode(DATA_PIN, OUTPUT);
  pinMode(CLOCK_PIN, OUTPUT);

  // TB6612FNG pins
  pinMode(PWM_PIN, OUTPUT);
  pinMode(STBY_PIN, OUTPUT);

  // Enable driver
  digitalWrite(STBY_PIN, HIGH);
  analogWrite(PWM_PIN, 255);  // full power (short pulses, safe)

  // Initialize 595 outputs LOW
  write595(0);
}

// Send 8-bit value to 74HC595
void write595(byte data) {
  digitalWrite(LATCH_PIN, LOW);
  shiftOut(DATA_PIN, CLOCK_PIN, MSBFIRST, data);
  digitalWrite(LATCH_PIN, HIGH);
}

// Set motor direction via AIN1/AIN2
void setDirection(bool ain1, bool ain2) {
  byte data = 0;
  if (ain1) data |= (1 << AIN1_BIT);
  if (ain2) data |= (1 << AIN2_BIT);
  write595(data);
}

// Pulse solenoid in one direction
void pulseSolenoid(bool forward) {
  if (forward) {
    setDirection(HIGH, LOW);
  } else {
    setDirection(LOW, HIGH);
  }

  delay(PULSE_MS);      // 20ms pulse
  setDirection(LOW, LOW); // stop
}

void loop() {
  for (int i = 0; i < CYCLES; i++) {
    pulseSolenoid(true);    // forward
    delay(WAIT_MS);

    pulseSolenoid(false);   // backward
    delay(WAIT_MS);
  }

  // Stop forever
  setDirection(LOW, LOW);
  while (1);
}
*/

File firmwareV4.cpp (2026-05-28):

const int LATCH_PIN = 10;
const int DATA_PIN  = 11;
const int CLOCK_PIN = 13;

const int PWM_PIN   = 9;
const int STBY_PIN  = 12;

const int ROWS = 3;
const int COLS = 6;

const int NUM_595 = 5;

const int PULSE_MS = 10;

const int MAX_BATCH = 12;

const unsigned long LONG_PRESS_MS = 600;

byte regs[NUM_595] = {0,0,0,0,0};

bool currentState[3][6];

bool buttonState[3][6];
bool longSent[3][6];

unsigned long pressStart[3][6];

const int rowPins[3] = {2,3,4};
const int colPins[6] = {5,6,7,8,A0,A1};

struct SolenoidMap {

  int regIndex;
  int bitRaise;
  int bitLower;
};

SolenoidMap solenoids[18] = {

  {1,0,1},
  {1,2,3},
  {1,4,5},
  {1,6,7},

  {2,0,1},
  {2,2,3},
  {2,4,5},
  {2,6,7},

  {3,0,1},
  {3,2,3},
  {3,4,5},
  {3,6,7},

  {-1,-1,-1},
  {-1,-1,-1},
  {-1,-1,-1},
  {-1,-1,-1},
  {-1,-1,-1},
  {-1,-1,-1}
};

void setup() {

  Serial.begin(115200);

  pinMode(LATCH_PIN, OUTPUT);
  pinMode(DATA_PIN, OUTPUT);
  pinMode(CLOCK_PIN, OUTPUT);

  pinMode(PWM_PIN, OUTPUT);
  pinMode(STBY_PIN, OUTPUT);

  digitalWrite(STBY_PIN, LOW);

  analogWrite(PWM_PIN, 255);

  digitalWrite(STBY_PIN, HIGH);

  clearAllRegisters();

  for (int r = 0; r < ROWS; r++) {

    pinMode(rowPins[r], OUTPUT);

    digitalWrite(rowPins[r], HIGH);
  }

  for (int c = 0; c < COLS; c++) {

    pinMode(colPins[c], INPUT_PULLUP);
  }

  for (int r = 0; r < ROWS; r++) {

    for (int c = 0; c < COLS; c++) {

      currentState[r][c] = false;

      buttonState[r][c] = false;

      longSent[r][c] = false;

      pressStart[r][c] = 0;
    }
  }

  Serial.println("READY");
}

void loop() {

  handleSerialInput();

  scanButtons();
}

void handleSerialInput() {

  if (!Serial.available())
    return;

  String line =
    Serial.readStringUntil('\n');

  line.trim();

  if (line.length() != 18)
    return;

  bool newPattern[3][6];

  int index = 0;

  for (int r = 0; r < ROWS; r++) {

    for (int c = 0; c < COLS; c++) {

      newPattern[r][c] =
        (line[index] == '1');

      index++;
    }
  }

  applyPattern(newPattern);
}

void applyPattern(bool newPattern[3][6]) {

  int batchCount = 0;

  clearAllRegisters();

  for (int r = 0; r < ROWS; r++) {

    for (int c = 0; c < COLS; c++) {

      bool oldState =
        currentState[r][c];

      bool newState =
        newPattern[r][c];

      if (oldState == newState)
        continue;

      int index =
        r * 6 + c;

      if (newState) {

        activateSolenoid(
          index,
          true
        );

      } else {

        activateSolenoid(
          index,
          false
        );
      }

      currentState[r][c] =
        newState;

      batchCount++;

      if (batchCount >= MAX_BATCH) {

        pulseRegisters();

        batchCount = 0;
      }
    }
  }

  if (batchCount > 0) {

    pulseRegisters();
  }
}

void pulseRegisters() {

  writeAllRegisters();

  delay(PULSE_MS);

  clearAllRegisters();

  delay(6);
}

void scanButtons() {

  for (int r = 0; r < ROWS; r++) {

    digitalWrite(rowPins[r], LOW);

    for (int c = 0; c < COLS; c++) {

      bool pressed =
        digitalRead(colPins[c]) == LOW;

      if (
        pressed &&
        !buttonState[r][c]
      ) {

        buttonState[r][c] = true;

        longSent[r][c] = false;

        pressStart[r][c] = millis();
      }

      else if (
        !pressed &&
        buttonState[r][c]
      ) {

        buttonState[r][c] = false;

        if (!longSent[r][c]) {

          Serial.print("SHORT:");
          Serial.print(r);
          Serial.print(",");
          Serial.println(c);
        }
      }

      else if (
        pressed &&
        buttonState[r][c] &&
        !longSent[r][c]
      ) {

        if (
          millis() - pressStart[r][c]
          > LONG_PRESS_MS
        ) {

          longSent[r][c] = true;

          Serial.print("LONG:");
          Serial.print(r);
          Serial.print(",");
          Serial.println(c);
        }
      }
    }

    digitalWrite(rowPins[r], HIGH);
  }
}

void activateSolenoid(
  int index,
  bool raise
) {

  if (index < 0 || index >= 18)
    return;

  SolenoidMap s =
    solenoids[index];

  if (s.regIndex == -1)
    return;

  if (raise) {

    regs[s.regIndex] |=
      (1 << s.bitRaise);

  } else {

    regs[s.regIndex] |=
      (1 << s.bitLower);
  }
}

void writeAllRegisters() {

  digitalWrite(LATCH_PIN, LOW);

  for (
    int i = NUM_595 - 1;
    i >= 0;
    i--
  ) {

    shiftOut(
      DATA_PIN,
      CLOCK_PIN,
      MSBFIRST,
      regs[i]
    );
  }

  digitalWrite(LATCH_PIN, HIGH);
}

void clearAllRegisters() {

  for (int i = 0; i < NUM_595; i++) {

    regs[i] = 0;
  }

  writeAllRegisters();
}

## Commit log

2025-11-27 finished schematic for each module!!
    [Tactile Browser.kicad_pcb, Tactile Browser.kicad_sch, Tactile-Browser-Keycaps.kicad_pcb, Tactile-Browser-Keycaps.kicad_sch]
2025-11-28 more sidebar progress
    [Sidebar.kicad_sch]
2025-12-19 sidebar progress
    [Sidebar.kicad_sch]
2025-12-20 electrical safety
    [Sidebar.kicad_sch]
2026-01-05 moved all solenoids to 74hc595s
    [Tactile Browser.kicad_sch]
2026-01-06 added footprints to module
    [Tactile Browser.kicad_sch]
2026-01-06 pcb edits + updated driver footprint
    [Tactile Browser.kicad_pcb, Tactile Browser.kicad_sch]
2026-01-06 pcb edits
    [Tactile Browser.kicad_pcb, Tactile Browser.kicad_sch]
2026-01-07 board testing
2026-01-19 2nd module iteration
    downsizing, dedicated SPI connectors, rearrangeable products
    [Tactile Browser.kicad_pcb, Tactile Browser.kicad_sch]
2026-01-19 updated module schematic
    [Tactile Browser.kicad_sch]
2026-02-06 updated solenoid/keyswitch connectors
    for ease of manufacturing
    [Sidebar.kicad_sch, Tactile Browser.kicad_pcb, Tactile Browser.kicad_sch]
2026-02-06 pcb design
    [Tactile Browser.kicad_pcb]
2026-02-06 actually fit everything onto the board I'm a genuis
    [Tactile Browser.kicad_pcb]
2026-02-06 made pcb even smaller
    [Tactile Browser.kicad_pcb]
2026-02-07 Fixed huge solenoid netting issue
    [Tactile Browser.kicad_pcb, Tactile Browser.kicad_sch]
2026-02-07 a ton of work on the pcb
    [Tactile Browser.kicad_sch]
2026-02-09 integrated drivers
    added schottky diodes, bulk & decoupling capacitors
    [Tactile Browser.kicad_pcb, Tactile Browser.kicad_sch]
2026-02-09 updated pcb
    [Tactile Browser.kicad_pcb]
2026-02-13 updated capacitors
    [Tactile Browser.kicad_sch]
2026-02-14 changed to vertical screw terminals
    [Tactile Browser.kicad_sch, pxc_1935310_07_02_PT-1-5-2-5-0-V_3D.stp]
2026-02-14 solenoid wiring!!
    [Tactile Browser.kicad_pcb, Tactile Browser.kicad_sch]
2026-02-14 made the board even smaller!
    [Tactile Browser.kicad_pcb]
2026-02-14 capacitor naming scheme
    [Tactile Browser.kicad_pcb, Tactile Browser.kicad_sch]
2026-02-15 schottky diode placement
    [Tactile Browser.kicad_pcb, Tactile Browser.kicad_sch]
2026-02-15 more work on pcb
2026-02-15 PCB almost done!
    [Tactile Browser.kicad_pcb, Tactile Browser.kicad_sch]
2026-02-16 more pcb work
    [Tactile Browser.kicad_pcb]
2026-02-16 almost done with pcb!
    [Tactile Browser.kicad_pcb]
2026-02-16 ground +12V planes
    [Tactile Browser.kicad_pcb]
2026-02-19 ran drc, finished routing
    [Tactile Browser.kicad_pcb]
2026-03-02 FINISHED PCB
    resolved DRC, added drill holes,
    [Tactile Browser.kicad_pcb]
2026-03-02 prepped pcb for assembly
    [TB_Module_BOM.csv, TB_Module_CPL_Merged.csv, Tactile Browser-12V_Cu.gbr, Tactile Browser-B_Cu.gbr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]
2026-03-02 S_out vias
    [TB_Module_BOM.csv, Tactile Browser-12V_Cu.gbr, Tactile Browser-B_Cu.gbr, Tactile Browser-B_Mask.gbr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]
2026-03-23 sidebar updates
    [Sidebar.kicad_sch]
2026-03-23 finished with sidebar schematic!
    [Sidebar.kicad_sch]
2026-03-24 finished footprints (mostly)
    [Sidebar.kicad_sch, Tactile Browser.kicad_sch]
2026-03-24 started sidebar pcb
    [Sidebar.kicad_pcb, Sidebar.kicad_sch]
2026-03-24 finished pcb placement
    [Sidebar.kicad_pcb]
2026-03-25 added power mosfet
    [Sidebar.kicad_sch]
2026-03-25 correct mosfet footprints
    [Sidebar.kicad_sch]
2026-03-25 finally got the right fuse
    [Sidebar.kicad_pcb, Sidebar.kicad_sch]
2026-03-25 footprint placement
    [Sidebar.kicad_pcb]
2026-03-25 sidebar pcb progress
    [Sidebar.kicad_pcb]
2026-03-25 done with pcb connections
    [Sidebar.kicad_pcb, Sidebar.kicad_sch]
2026-03-25 finished filled zones! (sidebar)
    [Sidebar.kicad_pcb]
2026-03-25 FINISHED SIDEBAR
    [Sidebar.kicad_pcb]
2026-03-25 added m2 screws
    [Sidebar.kicad_pcb]
2026-03-26 finished keyswitch
    [Tactile-Browser-Keycaps.kicad_pcb]
2026-03-26 prep for manufacturing
    [Sidebar-merged-pos.csv, Sidebar_JLCPCB_CPL_Merged.csv]
2026-05-27 Module prototype
    I still need to upload the 3d files for the casings I made, but the main thing is over the past few months I've ordered and soldered all the pcbs and they are all working!! I should've uploaded more 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
    [Sidebar.kicad_pcb, TB_Module_CPL.csv, TB_Module_CPL_Merged.csv]
